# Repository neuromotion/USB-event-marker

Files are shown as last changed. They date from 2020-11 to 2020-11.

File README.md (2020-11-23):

# USB Event Marker

Use an arduino-compatible `Teensy 3.2` board to output 8-channel digital event markers from a computer to a data acquisition system. When the board receives an event code, one or more of the 8 pins will output a short pulse simultaneously. The different combinations of 8 pins can encode 255 distinct event codes in binary, for identifying different types of events.

As of 12/2018, only the first 5 output pins are connected to OpenEphys analog input channels. That means that only the numbers in the range [1, 31] are valid event codes.

This repository contains:

- Firmware for the `Teensy 3.2` board, which will listen for events over the USB serial connection. 

- Eagle schematic showing how to connect the 5 teensy output pins to an RJ45 (ethernet) jack (that can then be broken out to the analog inputs on any electrophysiology rig)

- Eagle schematic showing how to connect a photodiode to an RJ45 (ethernet) jack (that can then be broken out to the analog input on any electrophysiology rig)

- 3D schematics of a case (bottom and top) to hold the teensy and RJ45 jack

- 3D schematic of a case to hold the photodiode

- `find_event_marker_port.py`: A python script for finding the path to your USB Event Marker's serial port, configuring it using `stty`, and then printing the path to it. Other programs can run this script to get the path, and then writing single-byte event codes to it as if it was a normal binary file. 

- `example.py`:  An example python script for sending events to the USB Event Marker, by opening it as a binary file. 

## Shopping list

### Event Marker

- teensyduino 3.2 board: https://www.sparkfun.com/products/13736
- RJ45 jack: https://www.sparkfun.com/products/8534
- RJ45 breakout: https://www.sparkfun.com/products/716

### Photodiode

- Photodiode (OPT101PG4): https://www.digikey.com/en/products/detail/texas-instruments/OPT101PG4/1899803
- RJ45 jack: https://www.sparkfun.com/products/8534
- RJ45 breakout: https://www.sparkfun.com/products/716
- monitor clip: https://www.amazon.com/COOK-COLOR-Black-Magnetic-Plastic/dp/B07CZ3ZYSX/

## Installation

### Firmware

If you need to make a new USB Event Marker board or update the firmware of an existing one, follow these instructions.

1. Install the [Arduino IDE](https://www.arduino.cc/en/Main/Software). You must install the offline IDE version, instead of using the online "Arduino Create" tool.

2. Install the [Teensyduino](https://www.pjrc.com/teensy/teensyduino.html) add-on to the Arduino IDE, to support the `Teensy 3.2` board.

3. Connect the device to the computer with a USB cable, if it wasn't already plugged in.

4. Launch the Arduino IDE. 

5. Open the file `usb-event-marker.ino`. 

6. In the menu bar, select `Tools -> Board: -> "Teensy 3.2/3.1"`. 

7. Select `Tools -> USB Type: -> "Serial + Keyboard + Mouse + Joystick"`.

8. Select `Tools -> CPU Speed: -> "96 MHz"`.

9. Go to `Tools -> Port` and select which port the device is connected to. The port name will vary, but might look something like `/dev/cu.usbmodem*` on a Mac, or `/dev/ttyACM*` in linux. You can check by unplugging the device and seeing which entry in the port list disappears.

10. Compile and upload the firmware by clicking the round arrow button, or by selecting `Sketch -> Upload` in the menu bar. Look for messages printed in the bottom part of the window. If the upload was successful, you can now use the reconfigured device. 

### Host Computer

The included `find_event_marker_port.py` script makes it simple to send events to the device from a host computer. It requires:

- linux
- the `stty` utility (should already be installed on Ubuntu)
- python3 (should already be installed on Ubuntu)
- the pyserial library (`$ pip3 install pyserial`)

If you cannot meet these requirements (eg. on Windows), you should be able to replicate the functionality of `find_event_marker_port.py` using other tools.

After installing the above requirements, add your username (`evan`) to the group (`dialout`) that's allowed to access serial ports:

    sudo usermod -a -G dialout evan

Reboot the computer to let this change take effect.

Plug the USB Event Marker device into one of the computer's USB ports and try running the example script:

    python3 example.py

You should see the device's light flash every time an event code is sent. If you watch the device's outputs with an oscilloscope, OpenEphys, or other data acquisition system, you should see pulses encoding each event code's value in binary.

## Sending Events 

See `example.py` for a simple example of how to send event codes to the USB Event Marker device
from a python script.

To send events from your application in any other language:

 1. Run `find_event_marker_port.py` to configure the serial port and get the path to its file.
 2. Open the file as a writable, binary file.
 3. Write individual bytes (event codes) to the file.
 4. Close the file when your application is all finished running.

See these task repos for examples in [matlab](https://github.com/neuromotion/matlab-msit-task) and [javascript](https://github.com/neuromotion/resting-state-task).

## Firmware Configuration and Timing 

The firmware's `ALWAYS_PULSE_MASK` feature lets you force certain pins to always pulse on every event, regardless of the event code value. We use this to make an LED connected to the 8th pin flash whenever an event is received. That's useful for debugging and for synchronizing events with video, but limits the highest unique event code to 127, instead of 255. (Note that the highest event code will be limited even further if fewer than 7 of the output pins are connected to your data acquisition system, like in the 2018 Cube wiring.)

Try not to send two event markers that are closer together than the length of the pulse (10ms by default, controlled by `pulse_milliseconds` in the firmware). If you do, you'll see two full pulses with a very short gap between them (~10us by default, controlled by `gap_microseconds`). So it will look as though the second event happened right after the first pulse ended, even though in reality, it happened earlier than that.

Make sure that `pulse_milliseconds` and `gap_microseconds` are long enough to be comfortably detected at your data acquisition system's sample rate.

Latency and jitter between an event in an application and an output pulse will depend mostly on delays within the host computer. Latency has not been characterized. 

### Test of jitter: 

* Used: 
    - a Teensy 3.2 with 96MHz clock
    - a chromebook running linux
    - commit 55cc48c of this repository
* Repeatedly send events using the included python script, sleeping for approximately 20ms in between. 
* After 5,000 recorded pulses:
    - Pulse width: 
        - min: 10.000ms
        - max: 10.004ms
        - std dev: 587ns
    - Gap between pulses: 
        - min: 10.173ms
        - max: 15.929ms
        - std dev: 92us

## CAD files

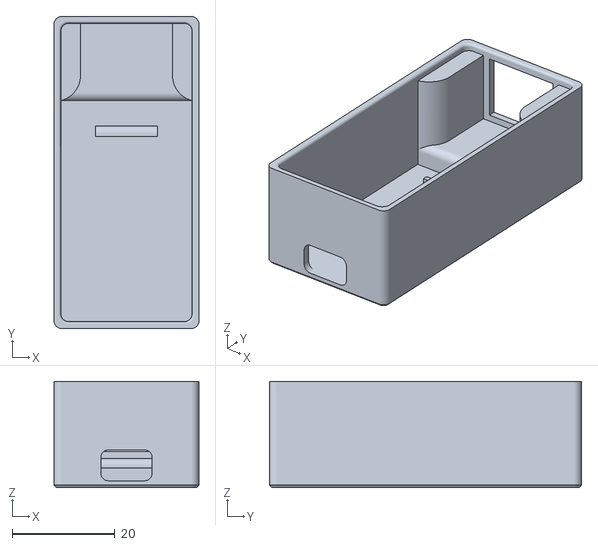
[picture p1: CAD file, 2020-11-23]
3d-parts/Event-marker-case-botton.stl
28.2 x 60.7 x 20.7

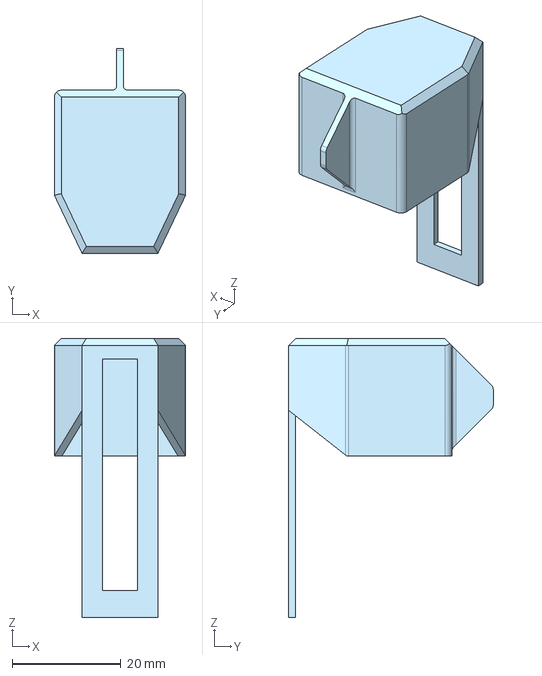
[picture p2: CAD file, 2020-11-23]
3d-parts/Photodiode-case.step
24.1 x 37.6 x 51.3 mm

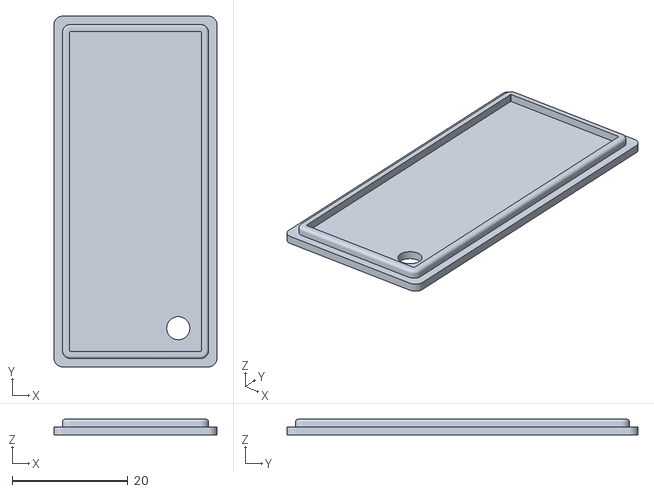
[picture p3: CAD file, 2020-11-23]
3d-parts/Event-marker-case-top.stl
28.2 x 60.7 x 2.70
